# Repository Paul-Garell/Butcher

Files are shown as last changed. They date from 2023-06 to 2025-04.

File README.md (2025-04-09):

# Butcher Lab Cervicheck project

Questions, reach out to George Zeng (gz266@cornell.edu). 

This contains the code to run on Arduino Uno/Due to calculate frequency sweeps using the AD5933 chip.

This repo also will contain the code for communication between the Rasberry pi and Arduino. 

PCB board designs can be found under hardware. 

Uno code (working) can be found under Arduino

Raspberry Pi information can be found under RasPi

Contains code to analyze and present data

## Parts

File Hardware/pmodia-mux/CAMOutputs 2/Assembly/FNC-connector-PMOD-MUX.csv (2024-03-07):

Qty | Value | Device | Package | Parts | Description | AVAILABILITY | CHECK_PRICES | DESCRIPTION | MF | MP | MPN | OC_FARNELL | OC_NEWARK | PACKAGE | POPULARITY | PRICE | PROD_ID | PURCHASE-URL | SNAPEDA_LINK | SPICEPREFIX | VALUE
1 |  | PINHD-1X7/90 | 1X07/90 | JP1 | PIN HEADER |  |  |  |  |  |  |  |  |  | 1
1 | 0.1uF | 0.1UF-0603-25V-(+80/-20%) | 0603 | C1 | 0.1µF ceramic capacitors |  |  |  |  |  |  |  |  |  |  |  | CAP-00810 |  |  |  | 0.1uF
6 | 0.1uF | C-USC0805K | C0805K | C2, C4, C17, C18, C23, C24 | CAPACITOR, American symbol |  |  |  |  |  |  |  |  |  | 19 |  |  |  |  | C
1 | 100K | R-US_R0603 | R0603 | R17 | RESISTOR, American symbol |  |  |  |  |  |  |  |  |  | 77 |  |  |  |  | R
1 | 10k | 10KOHM-0603-1/10W-1% | 0603 | R1 | 10kΩ resistor |  |  |  |  |  |  |  |  |  |  |  | RES-00824 |  |  |  | 10k
5 | 10uF | C-USC0805K | C0805K | C3, C15, C16, C20, C25 | CAPACITOR, American symbol |  |  |  |  |  |  |  |  |  | 19 |  |  |  |  | C
1 | 20 | R-US_R0603 | R0603 | R15 | RESISTOR, American symbol |  |  |  |  |  |  |  |  |  | 77 |  |  |  |  | R
2 | 20K | R-US_R0603 | R0603 | R16, R18 | RESISTOR, American symbol |  |  |  |  |  |  |  |  |  | 77 |  |  |  |  | R
1 | 300 | 0.3OHM-0805-1/8W-1% | 0805 | R10 | 0.3Ω resistor |  |  |  |  |  |  |  |  |  |  |  | RES-11622 |  |  |  | 0.3
1 | 47nF | C-USC0805K | C0805K | C19 | CAPACITOR, American symbol |  |  |  |  |  |  |  |  |  | 19 |  |  |  |  | C
4 | 49.9K | R-US_R0603 | R0603 | R11, R12, R13, R14 | RESISTOR, American symbol |  |  |  |  |  |  |  |  |  | 77 |  |  |  |  | R
2 | 74HC4051BQ | 74HC4051BQ | DHVQFN-16-2.5X3.5MM | U1, U2 | NXP 74HC4051 8-Channel Analog Multiplexer/Demultiplexer |  |  |  |  |  |  |  |  |  |  |  | IC-13334
1 | AD5933 | AD5933 | SSOP16 | U3 | 1 MSPS, 12-Bit Impedance Converter, Network Analyzer
1 | AD8606 | AD8606 | SOIC-8 | U4 | Operational amplifier; 10MHz; 2.7÷5VDC; Channels: 2; SO8 Check availability | In Stock | https://www.snapeda.com/parts/AD8606ARZ/Analog+Devices/view-part/?ref=eda | Precision, Low Noise, RRIO, CMOS Op Amp (Dual) | Analog Devices | AD8606ARZ |  |  |  | SOIC-8 Analog Devices |  | None |  | https://www.snapeda.com/api/url_track_click_mouser/?unipart_id=43414&manufacturer=Analog Devices&part_name=AD8606ARZ&search_term=ad8606 | https://www.snapeda.com/parts/AD8606ARZ/Analog+Devices/view-part/?ref=snap
1 | ADG849THROUHG_HOLE | ADG849THROUHG_HOLE | SOT65P210X110-6N | U$1
1 | ADP150 | ADP150 | SOT95P280X100-5N | U5 | IC REG LINEAR 2V 150MA 5TSOT Check availability | In Stock | https://www.snapeda.com/parts/ADP150AUJZ-2.0-R7/Analog+Devices/view-part/?ref=eda | Ultralow Noise, 150 mA CMOS Linear Regulator | Analog Devices | ADP150AUJZ-2.0-R7 |  |  |  | TSOT-5 Analog Devices |  | None |  | https://www.snapeda.com/api/url_track_click_mouser/?unipart_id=1225884&manufacturer=Analog Devices&part_name=ADP150AUJZ-2.0-R7&search_term=adp150 | https://www.snapeda.com/parts/ADP150AUJZ-2.0-R7/Analog+Devices/view-part/?ref=snap
1 | FH12-16S-0.5SH | FH12-16S-0.5SH | FH12-16S-0.5SH | X1 | 0.5mm Pitch Connectors For FPC/FFC |  |  |  |  |  | FH12-16S-0.5SH(55) | 1324546 | 34M6162 |  | 0

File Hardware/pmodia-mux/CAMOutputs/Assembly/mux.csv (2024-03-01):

Qty | Value | Device | Package | Parts | Description | MF | MPN | OC_FARNELL | OC_NEWARK | POPULARITY
1 | FH12-16S-0.5SH | FH12-16S-0.5SH | FH12-16S-0.5SH | X2 | 0.5mm Pitch Connectors For FPC/FFC |  | FH12-16S-0.5SH(55) | 1324546 | 34M6162 | 0
16 | PADPAD | PADPAD | PAD | U$1, U$2, U$3, U$4, U$5, U$6, U$7, U$8, U$9, U$10, U$11, U$12, U$13, U$14, U$15, U$16

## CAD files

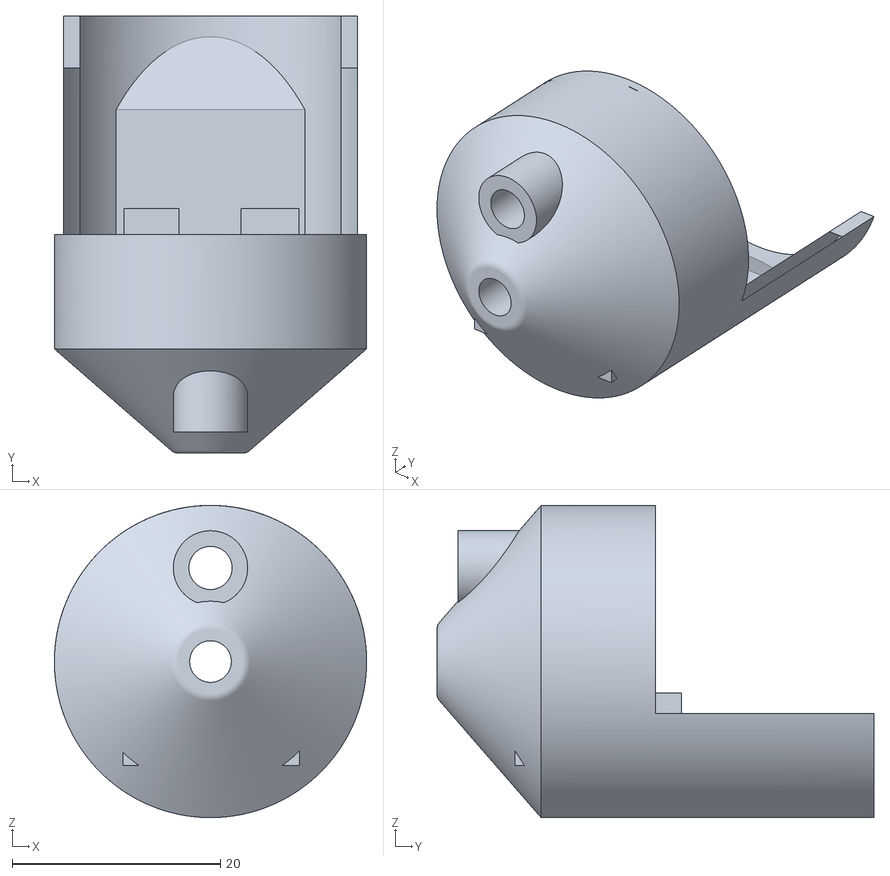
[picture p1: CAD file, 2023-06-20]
Hardware/Cervicheck Probe Tip V1 v20.1.stl
30.0 x 42.0 x 30.0

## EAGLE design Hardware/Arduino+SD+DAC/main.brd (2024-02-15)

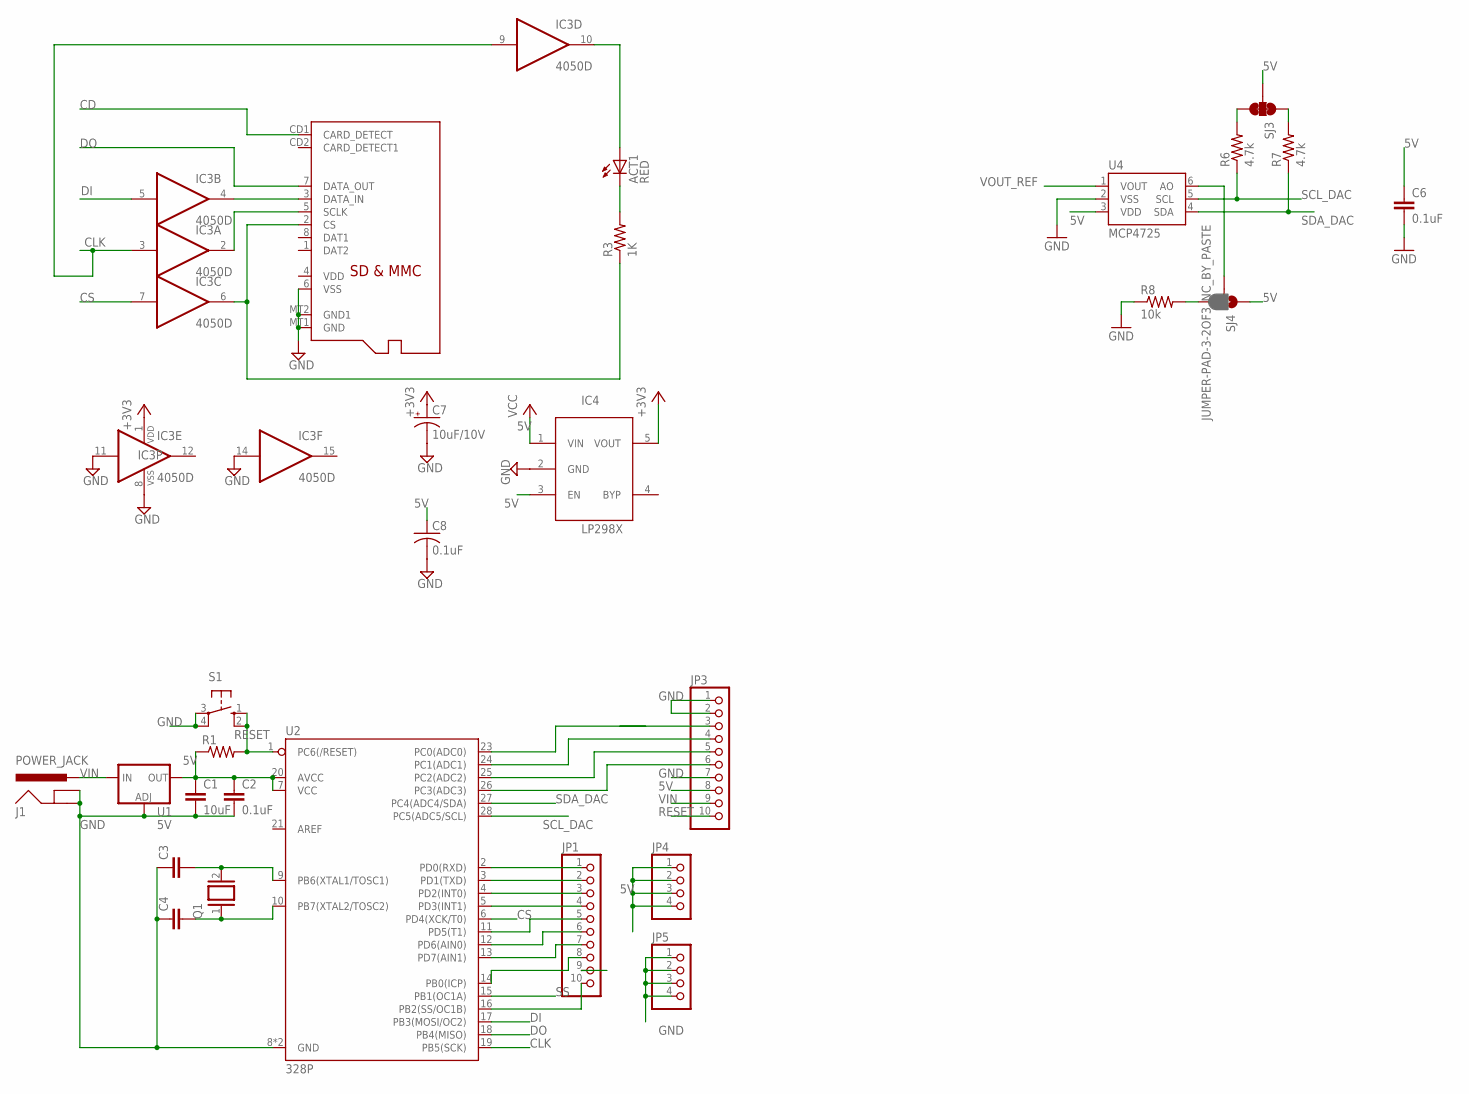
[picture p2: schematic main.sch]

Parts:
ACT1: RED; CHIP-LED0805
C1: 10uF; C025-024X044
C2: 0.1uF; C025-024X044
C3, C4: C-EU025-024X044; C025-024X044
C6: 0.1uF; 0603-CAP
C7: 10uF/10V; A/3216-18R
C8: 0.1uF; C0805K
IC3: 4050D; SO16
IC4: LP298XS; SOT23-5L
J1: POWER_JACK; POWER_JACK_PTH
JP1, JP3: PINHD-1X10; 1X10
JP4, JP5: PINHD-1X4; 1X04
Q1: XTAL/S; QS
R1: R-US_0204/7; 0204/7
R3: 1K; R0805
R6, R7: 4.7k; 0603-RES
R8: 10k; 0603-RES
S1: 10-XX; B3F-10XX
SJ3: JUMPER-PAD-3-NC_BY_TRACE; PAD-JUMPER-3-3OF3_NC_BY_TRACE_YES_SILK_FULL_BOX
SJ4: JUMPER-PAD-3-2OF3_NC_BY_PASTE; PAD-JUMPER-3-2OF3_NC_BY_PASTE_YES_SILK_FULL_BOX
U1: 5V; SOT223
U2: 328P; DIP28
U4: MCP4725; SOT23-6
X2: MICROSD

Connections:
5V: C1.1, C2.1, C6.1, C8.1, IC4.1 (VIN), IC4.3 (EN), JP3.8, JP4.1, JP4.2, JP4.3, JP4.4, R1.1, SJ3.2, SJ4.1, U1.2 (OUT), U1.4 (OUT), U2.7 (VCC), U2.20 (AVCC), U4.3 (VDD)
+3V3: C7.+, IC3.1 (VDD), IC4.5 (VOUT)
CD: X2.CD1 (CARD_DETECT)
CLK: IC3.3 (I), IC3.9 (I), U2.19 (PB5(SCK))
CS: IC3.7 (I), U2.6 (PD4(XCK/T0))
DI: IC3.5 (I), U2.17 (PB3(MOSI/OC2))
DO: U2.18 (PB4(MISO)), X2.7 (DATA_OUT)
GND: C1.2, C2.2, C3.1, C4.1, C6.2, C7.-, C8.2, IC3.8 (VSS), IC3.11 (I), IC3.14 (I), IC4.2 (GND), J1.GND, J1.GNDBREAK, JP3.1, JP3.2, JP3.7, JP5.1, JP5.2, JP5.3, JP5.4, R8.1, S1.3, S1.4 (P1), U1.1 (ADJ), U2.8 (GND), U2.22 (GND), U4.2 (VSS), X2.6 (VSS), X2.MT1 (GND), X2.MT2 (GND1)
unnamed: JP1.1, U2.2 (PD0(RXD))
unnamed: JP3.5, U2.25 (PC2(ADC2))
unnamed: C3.2, Q1.2, U2.9 (PB6(XTAL1/TOSC1))
unnamed: C4.2, Q1.1, U2.10 (PB7(XTAL2/TOSC2))
unnamed: JP1.2, U2.3 (PD1(TXD))
unnamed: JP1.3, U2.4 (PD2(INT0))
unnamed: JP3.6, U2.26 (PC3(ADC3))
unnamed: JP1.4, U2.5 (PD3(INT1))
unnamed: JP1.5, U2.11 (PD5(T1))
unnamed: R7.2, SJ3.1
unnamed: R6.2, SJ3.3
unnamed: SJ4.2, U4.6 (AO)
unnamed: R8.2, SJ4.3
unnamed: JP1.6, U2.12 (PD6(AIN0))
unnamed: JP1.7, U2.13 (PD7(AIN1))
unnamed: JP1.8, U2.14 (PB0(ICP))
unnamed: JP1.10, U2.16 (PB2(SS/OC1B))
unnamed: JP3.4, U2.24 (PC1(ADC1))
unnamed: ACT1.A, IC3.10 (O)
unnamed: IC3.2 (O), X2.5 (SCLK)
unnamed: IC3.6 (O), R3.1, X2.2 (CS)
unnamed: ACT1.C, R3.2
unnamed: IC3.4 (O), X2.3 (DATA_IN)
RESET: JP3.10, R1.2, S1.1 (S), S1.2 (S1), U2.1 (PC6(/RESET))
SCL_DAC: R6.1, U2.28 (PC5(ADC5/SCL)), U4.5 (SCL)
SDA_DAC: R7.1, U2.27 (PC4(ADC4/SDA)), U4.4 (SDA)
SS: JP1.9, U2.15 (PB1(OC1A))
VIN: J1.PWR, JP3.9, U1.3 (IN)
VOUT_REF: U4.1 (VOUT)

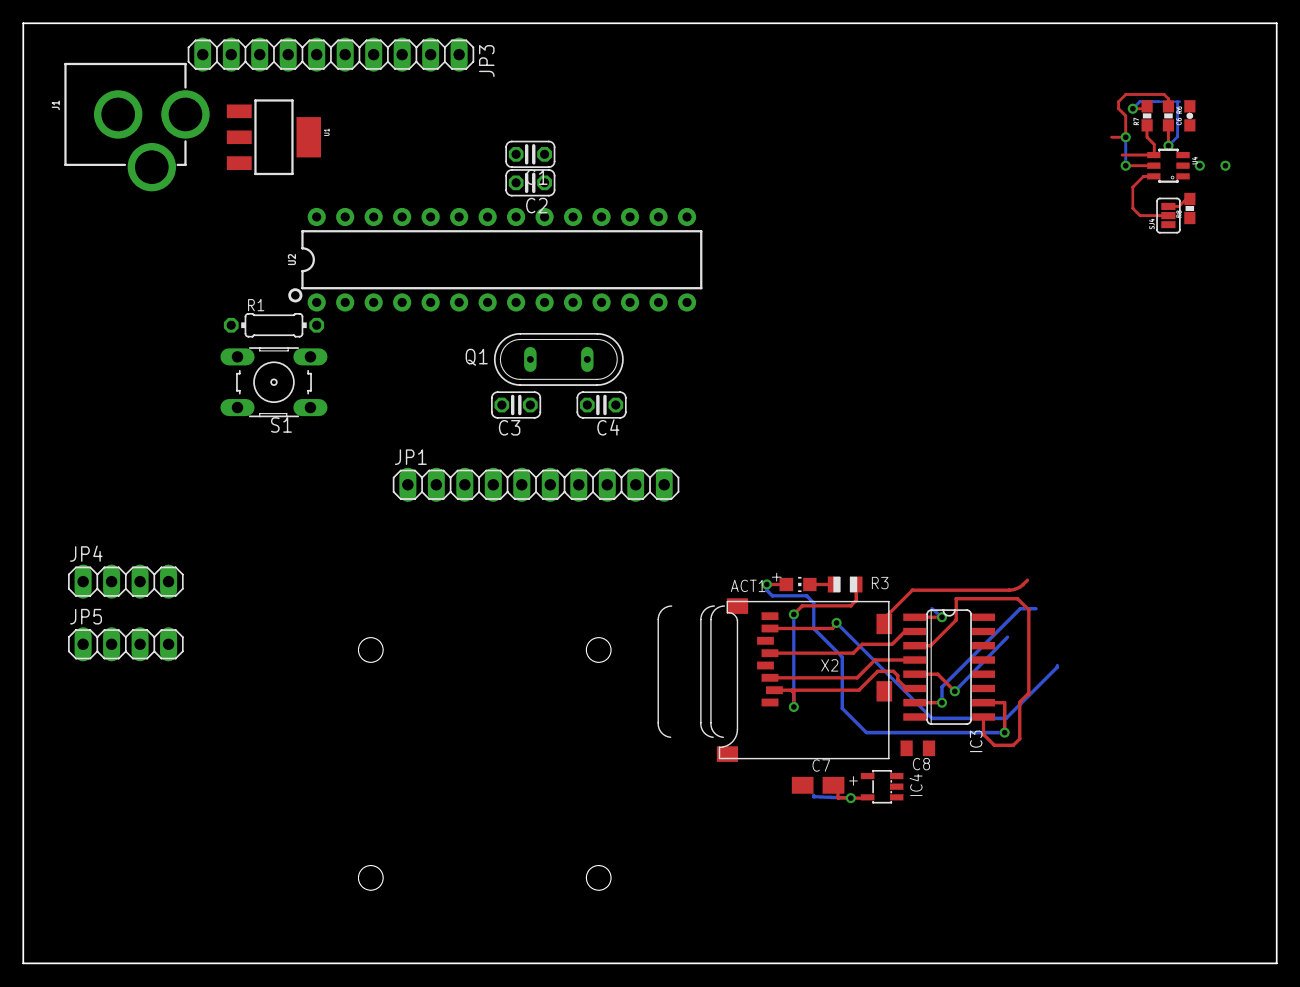
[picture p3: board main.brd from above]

Board: 2 copper layers, 111.8 x 83.8 mm, 28 parts (1 on the bottom side), 35 nets.

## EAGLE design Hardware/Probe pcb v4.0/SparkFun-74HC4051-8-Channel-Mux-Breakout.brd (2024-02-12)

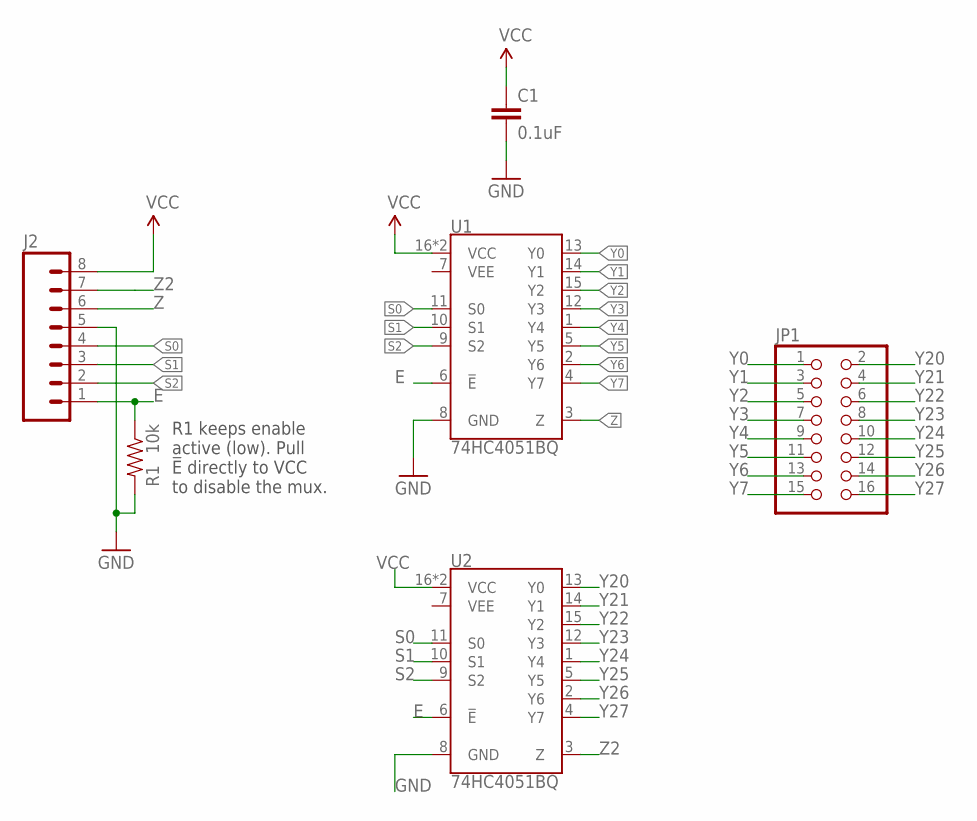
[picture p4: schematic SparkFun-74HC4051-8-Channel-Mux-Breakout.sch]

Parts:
C1: 0.1uF; 0603
J2: M08; 1X08_ROUND
JP1: PINHD-2X8; 2X08
R1: 10k; 0603
U1, U2: 74HC4051BQ; DHVQFN-16-2.5X3.5MM

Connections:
E: J2.1, R1.1, U1.6 (!E!), U2.6 (!E!)
GND: C1.2, J2.5, R1.2, U1.8 (GND), U2.8 (GND)
S0: J2.4, U1.11 (S0), U2.11 (S0)
S1: J2.3, U1.10 (S1), U2.10 (S1)
S2: J2.2, U1.9 (S2), U2.9 (S2)
VCC: C1.1, J2.8, U1.16 (VCC), U1.EP (VCC), U2.16 (VCC), U2.EP (VCC)
Y0: JP1.1, U1.13 (Y0)
Y1: JP1.3, U1.14 (Y1)
Y2: JP1.5, U1.15 (Y2)
Y3: JP1.7, U1.12 (Y3)
Y4: JP1.9, U1.1 (Y4)
Y5: JP1.11, U1.5 (Y5)
Y6: JP1.13, U1.2 (Y6)
Y7: JP1.15, U1.4 (Y7)
Y20: JP1.2, U2.13 (Y0)
Y21: JP1.4, U2.14 (Y1)
Y22: JP1.6, U2.15 (Y2)
Y23: JP1.8, U2.12 (Y3)
Y24: JP1.10, U2.1 (Y4)
Y25: JP1.12, U2.5 (Y5)
Y26: JP1.14, U2.2 (Y6)
Y27: JP1.16, U2.4 (Y7)
Z: J2.6, U1.3 (Z)
Z2: J2.7, U2.3 (Z)

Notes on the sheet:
R1 keeps enable active (low). Pull !E! directly to VCC to disable the mux.

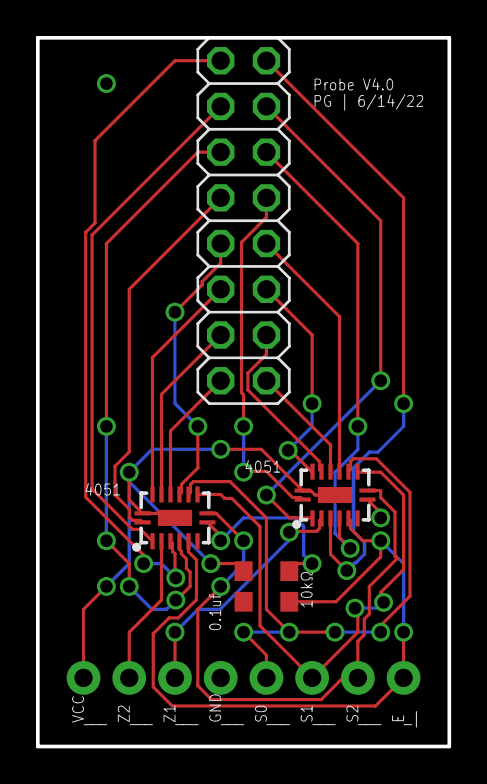
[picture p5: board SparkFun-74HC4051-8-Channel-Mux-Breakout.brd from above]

Board: 2 copper layers, 22.9 x 39.4 mm, 6 parts (1 on the bottom side), 24 nets.

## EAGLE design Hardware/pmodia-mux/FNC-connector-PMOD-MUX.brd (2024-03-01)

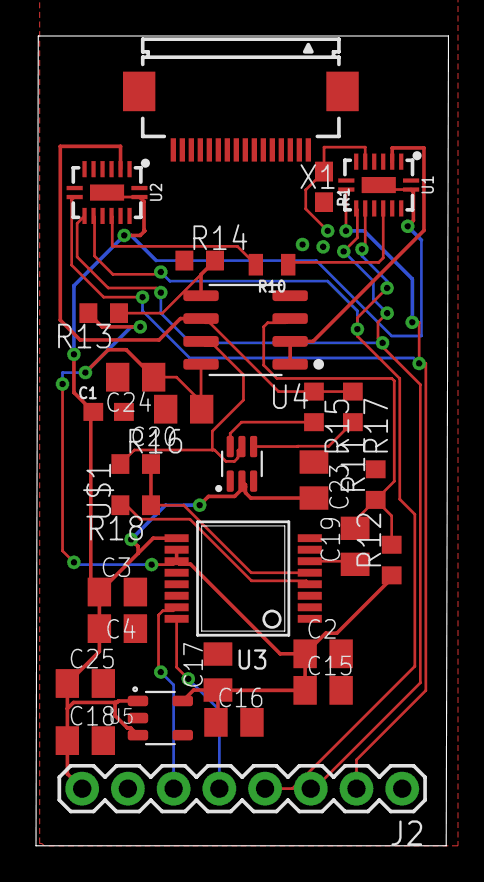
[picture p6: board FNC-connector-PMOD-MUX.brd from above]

Board: 2 copper layers, 22.9 x 45.0 mm, 31 parts (0 on the bottom side), 35 nets.

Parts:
C1: 0.1uF; 0603
C2, C4, C17, C18, C23, C24: 0.1uF; C0805K
C3, C15, C16, C20, C25: 10uF; C0805K
C19: 47nF; C0805K
J2: 1X08_ROUND
R1: 10k; 0603
R10: 300; 0805
R11, R12, R13, R14: 49.9K; R0603
R15: 20; R0603
R16, R18: 20K; R0603
R17: 100K; R0603
U1, U2: 74HC4051BQ; DHVQFN-16-2.5X3.5MM
U3: AD5933; SSOP16
U4: AD8606; SOIC-8
U5: ADP150; SOT95P280X100-5N
U$1: ADG849THROUHG_HOLE; SOT65P210X110-6N
X1: FH12-16S-0.5SH

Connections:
E: R1.1, U1.6, U2.6
GND: C1.2, C2.2, C3.2, C4.2, C15.2, C16.2, C17.2, C18.2, C20.2, C23.1, C24.2, C25.2, J2.1, R1.2, R11.2, R14.1, U1.8, U2.8, U3.12, U3.14, U4.4, U5.2, U$1.3
INBP: R13.1, R14.2, U4.5
unnamed: C19.1, U3.6
unnamed: C19.2, R11.1, R12.2, U4.3
unnamed: R18.2, U3.4
unnamed: R15.2, U$1.6
unnamed: R17.2, U$1.4
unnamed: R16.1, U4.7, U$1.5
S0: J2.4, U1.11, U2.11
S1: J2.3, U1.10, U2.10
S2: J2.2, U1.9, U2.9
SCL: J2.5, U3.16
SDA: J2.6, U3.15
VCC: C1.1, C3.1, C4.1, C18.1, C23.2, C25.1, J2.8, U1.16, U1.EP, U2.16, U2.EP, U3.9, U5.1, U5.3, U$1.2
VCC3V0: C2.1, C15.1, C16.1, C17.1, C20.1, C24.1, R12.1, R13.2, U3.10, U3.11, U4.8, U5.5
VIN: R16.2, R18.1, U3.5
Y0: R10.1, U1.13, X1.8
Y1: U1.14, X1.7
Y2: U1.15, X1.6
Y3: U1.12, X1.5
Y4: U1.1, X1.4
Y5: U1.5, X1.3
Y6: U1.2, X1.2
Y7: U1.4, X1.1
Y20: R10.2, U2.13, X1.9
Y21: U2.14, X1.10
Y22: U2.15, X1.11
Y23: U2.12, X1.12
Y24: U2.1, X1.13
Y25: U2.5, X1.14
Y26: U2.2, X1.15
Y27: U2.4, X1.16
Z: U1.3, U4.1, U4.2
Z2: R15.1, R17.1, U2.3, U4.6

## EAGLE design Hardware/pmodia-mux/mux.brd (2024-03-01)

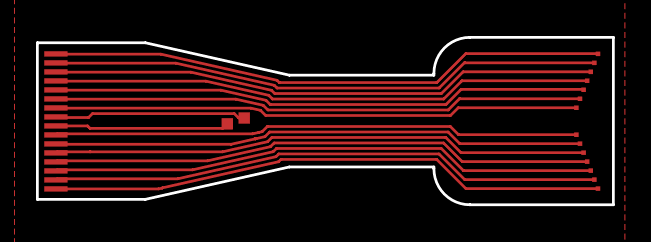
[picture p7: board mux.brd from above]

Board: 2 copper layers, 32.0 x 9.3 mm, 17 parts (0 on the bottom side), 16 nets.

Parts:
U$1, U$2, U$3, U$4, U$5, U$6, U$7, U$8, U$9, U$10, U$11, U$12, U$13, U$14, U$15, U$16: PADPAD; PAD
X2: FH12-16S-0.5SH

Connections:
unnamed: U$1.P$1, X2.1
unnamed: U$2.P$1, X2.2
unnamed: U$3.P$1, X2.3
unnamed: U$4.P$1, X2.4
unnamed: U$5.P$1, X2.5
unnamed: U$6.P$1, X2.6
unnamed: U$7.P$1, X2.7
unnamed: U$8.P$1, X2.8
unnamed: U$9.P$1, X2.9
unnamed: U$10.P$1, X2.10
unnamed: U$11.P$1, X2.11
unnamed: U$12.P$1, X2.12
unnamed: U$13.P$1, X2.13
unnamed: U$14.P$1, X2.14
unnamed: U$15.P$1, X2.15
unnamed: U$16.P$1, X2.16

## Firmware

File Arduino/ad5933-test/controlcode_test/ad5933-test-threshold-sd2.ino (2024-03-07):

#include <Wire.h>
#include "AD5933.h"
#include <Adafruit_MCP4725.h>
#include <SD.h>
#include <SPI.h>

#define START_FREQ  (10000)
#define FREQ_INCR   (5000)
#define NUM_INCR    (18)
#define REF_RESIST  (300)
#define DAC_RESOLUTION (9)

bool setter = true;
int follow = 0;

// Mux setup
int Signal = 5;
int i;
int sL[3] = {8, 9, 10};
int MUXtable[8][3] = {
  {0, 0, 0}, {1, 0, 0}, {0, 1, 0}, {1, 1, 0},
  {0, 0, 1}, {1, 0, 1}, {0, 1, 1}, {1, 1, 1}
};

// DAC setup for Pressure regulator
int DACp = 0;
double Curvoltage = .5;

Adafruit_MCP4725 dac;

double gain[NUM_INCR + 1];
int phase[NUM_INCR + 1];

// Pressure variable for barometric sensor
const int pressureInput = A1;  // where the pressure will be sensed
const int pressureZ = 102;    // the minimum voltage for 0 pressure
const int pressureM = 921;    // the maxium voltage for 15psi
const int pressurePSI = 15;  
float pressure;  // where we want to store the value from the incoming pressure transducer
int normalP = 0; // placeholder

File dataFile;
const double impedanceMax = 500.0; //CHANGED: threshold to detect air
bool impedanceCheck = false; 

String filename = "data.csv";
void setup(void)
{
  pinMode(Signal, OUTPUT);
  for (i = 0; i < 3; i++) pinMode(sL[i], OUTPUT);
  pinMode(A2, OUTPUT);
  digitalWrite(A2, LOW);
  dac.begin(0x60);
  
  // Begin serial at 9600 baud for output
  Serial.begin(9600);
  // Begin I2C
  Wire.begin();
  // Select SD card pin
  const int chipSelectPin = 4;
  // Perform initial configuration. Fail if any one of these fail.
  Serial.println("AD5933 Test Started!");

  if (!(AD5933::reset() &&
        AD5933::setInternalClock(true) &&
        AD5933::setStartFrequency(START_FREQ) &&
        AD5933::setIncrementFrequency(FREQ_INCR) &&
        AD5933::setNumberIncrements(NUM_INCR) &&
        AD5933::setPGAGain(PGA_GAIN_X1)))
  {
    Serial.println("FAILED in initialization!");
    while (true);
  }
  // Set mux to the calibration output (select Y0) (300 ohm resistor installed on board)
  digitalWrite(sL[0], MUXtable[0][0]);
  digitalWrite(sL[1], MUXtable[0][1]);
  digitalWrite(sL[2], MUXtable[0][2]);
  
  // Perform calibration sweep
  if (AD5933::calibrate(gain, phase, REF_RESIST, NUM_INCR + 1))
    Serial.println("Calibrated!");
  else
    Serial.println("Calibration failed...");

  // Initialize the SD card
  if (SD.begin(chipSelectPin)) {
    Serial.println("SD card module is connected.");
  } else {
    Serial.println("SD card module is not detected. Check connections.");
  }

  // Open a new file for writing
  dataFile = SD.open(filename, FILE_WRITE);
  if (dataFile) {
    Serial.println("Created data.csv file.");
  } else {
    Serial.println("Failed to create data.csv file!");
  }
  
  // Write the column headers to the file
  dataFile.println("Pin, Time, Pressure, Impedance");
  
  // Close the file
  dataFile.close();
}

int pinNum = 1;

void loop(void) {
  dac.setVoltage((Curvoltage * 4095) / 5, false);
  while (pinNum < 9) {
    selection(pinNum);
    if (frequencySweepEasy(pinNum)) break;
    pinNum++;
  }
  pinNum = 1;
  Curvoltage += .5;
  if (Curvoltage > 2.9) {
    Curvoltage = 0.5;
  }
}

bool frequencySweepEasy(int pin) {
  // Create arrays to hold the data
  int real[NUM_INCR + 1], imag[NUM_INCR + 1];

  // Perform the frequency sweep
  if (AD5933::frequencySweep(real, imag, NUM_INCR + 1)) {
    // Open the data file in append mode
    dataFile = SD.open("data.csv", FILE_WRITE);
    if (!dataFile) {
      // Calculating and printing out the pressure information
      int cfreq = START_FREQ / 1000;
      dataFile.print(pin);
      dataFile.print(", ");
      dataFile.print(millis());
      dataFile.print(", ");
      dataFile.print(normalP, 1);
      dataFile.print(", ");

      Serial.print(millis());
      Serial.print(", ");
      Serial.print(pin);
      Serial.print(", ");
      Serial.print(normalP, 1);

      for (int i = 0; i < NUM_INCR + 1; i++, cfreq += FREQ_INCR / 1000) {
        pressure = analogRead(pressureInput);
        pressure = (pressure - pressureZ) * 15 / (pressureM - pressureZ);
        normalP = abs((pressure * 6.89476) - 98);
        dataFile.print(", ");

        // Compute impedance
        double magnitude = sqrt(pow(real[i], 2) + pow(imag[i], 2));
        double impedance = 1 / (magnitude * gain[i]);

        dataFile.print(impedance);
        dataFile.print(", ");

        Serial.print(", ");
        Serial.print(impedance);
        Serial.println(" "); 

        // Determine if impedance is too high
        if (impedance > impedanceMax){ 
          Serial.print(" ");
          return true;
        }
      }
      dataFile.println(" ");
      Serial.println(" "); 
      // Close the file
      Serial.flush();
      dataFile.close();
    }
  }
  return false;
}

void selection(int j) {
  digitalWrite(sL[0], MUXtable[j][0]);
  digitalWrite(sL[1], MUXtable[j][1]);
  digitalWrite(sL[2], MUXtable[j][2]);
}

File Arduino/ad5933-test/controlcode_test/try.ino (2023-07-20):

#include <Wire.h>
#include "AD5933.h"
#include <Adafruit_MCP4725.h>

#define START_FREQ  (10000)
#define FREQ_INCR   (5000)
#define NUM_INCR    (18)
#define REF_RESIST  (300)

// Threshold setup
int impedanceCheck; // Define a high resistance here

// Mux setup
int Signal = 5;
int i;
int sL[3] = {8, 9, 10};
int MUXtable[8][3] = {
  {0, 0, 0}, {1, 0, 0}, {0, 1, 0}, {1, 1, 0},
  {0, 0, 1}, {1, 0, 1}, {0, 1, 1}, {1, 1, 1}
};

// DAC setup for Pressure regulator
int DACp = 0;
double Curvoltage = 0.5;

Adafruit_MCP4725 dac;
#define DAC_RESOLUTION (9)

double gain[NUM_INCR + 1];
int phase[NUM_INCR + 1];

// Pressure variable for barometric sensor
const int pressureInput = A1;
const int pressureZ = 102;
const int pressureM = 921;
const int pressurePSI = 15;
float pressure;
int normalP = 0;

void calibrateAD5933() {
  if (!(AD5933::reset() &&
        AD5933::setInternalClock(true) &&
        AD5933::setStartFrequency(START_FREQ) &&
        AD5933::setIncrementFrequency(FREQ_INCR) &&
        AD5933::setNumberIncrements(NUM_INCR) &&
        AD5933::setPGAGain(PGA_GAIN_X1)))
  {
    Serial.println("FAILED in initialization!");
    while (true) ;
  }

  if (AD5933::calibrate(gain, phase, REF_RESIST, NUM_INCR + 1)) {
    Serial.println("Calibrated!");
  } else {
    Serial.println("Calibration failed...");
  }

  // Store calibrated values in global variables
  int cfreq = START_FREQ / 1000; // Starting frequency
  for (int i = 0; i < NUM_INCR + 1; i++, cfreq += FREQ_INCR / 1000) {
    // Compute impedance
    double magnitude = sqrt(pow(gain[i], 2) + pow(phase[i], 2));
    gain[i] = 1 / (magnitude * gain[i]);
  }

  // Calculate and store the high impedance check value
  double magnitude = sqrt(pow(gain[0], 2) + pow(phase[0], 2));
  double impedance = 1 / (magnitude * gain[0]);
  impedanceCheck = (int)impedance;
}

void setup(void) {
  Serial.begin(9600);
  pinMode(Signal, OUTPUT);
  for (i = 0; i < 4; i++) pinMode(sL[i], OUTPUT);

  pinMode(A2, OUTPUT);
  digitalWrite(A2, LOW);
  dac.begin(0x60);
  Wire.begin();
  Serial.println("AD5933 Test Started!");

  // Call the calibration function once during setup
  calibrateAD5933();
}

int curChannel = 1;
void loop(void) {
  dac.setVoltage((Curvoltage * 4095) / 5, false);
  for (curChannel = 1; curChannel <= 8; curChannel++) {
    Serial.print(curChannel);
    selection(curChannel);
    if (frequencySweepEasy(curChannel)) break;
  }

  Curvoltage += 0.5; // Increment voltage counter
  if (Curvoltage > 2.9) {
    Curvoltage = 0.5;
  }
}

bool frequencySweepEasy(int pin) {
  // Create arrays to hold the data
  int real[NUM_INCR + 1], imag[NUM_INCR + 1];

  // Perform the frequency sweep
  if (AD5933::frequencySweep(real, imag, NUM_INCR + 1)) {
    // Print the frequency data
    int cfreq = START_FREQ / 1000;
    // Calculating and printing out the pressure information
    pressure = analogRead(pressureInput); // will read the value from the input pin
    pressure = (pressure - pressureZ) * 15 / (pressureM - pressureZ); // convert analog reading to psi
    normalP = abs((pressure * 6.89476) - 98); // normalize?

    Serial.print(millis());
    Serial.print(", ");
    Serial.print(pin);
    Serial.print(", ");
    Serial.print(normalP, 1); // converting to kPa while also printing (units kPa)

    for (int i = 0; i < NUM_INCR + 1; i++, cfreq += FREQ_INCR / 1000) {

      // Use the stored calibrated values to compute impedance
      double magnitude = sqrt(pow(real[i], 2) + pow(imag[i], 2));
      double impedance = 1 / (magnitude * gain[i]);
      Serial.print(", ");
      Serial.print(impedance);

      // Checker
      if (impedance > impedanceCheck) {
        Serial.println(" ");
        return true;
      }
    }
    Serial.println(" ");
  }
  return false;
}

void selection(int j) {
  digitalWrite(sL[0], MUXtable[j][0]);
  digitalWrite(sL[1], MUXtable[j][1]);
  digitalWrite(sL[2], MUXtable[j][2]);
}

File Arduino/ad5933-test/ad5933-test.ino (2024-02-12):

/*
  ad5933-test
    Reads impedance values from the AD5933 over I2C and prints them serially.
*/
// 200, 1.1, 5.1 20000
#include <Wire.h>
#include "AD5933.h"
#define START_FREQ  (10000)
#define FREQ_INCR   (5000)
#define NUM_INCR    (10) //was 18, changing to 10 for demo
#define REF_RESIST  (300)
bool setter = true;
int follow = 0;

//Mux setup
int Signal = 5; int i; //int n;
int sL[3] = {8, 9, 10}; //int sU[4] = {13,10,11,12};
int MUXtable[8][3] = {{0, 0, 0}, {1, 0, 0}, {0, 1, 0}, {1, 1, 0},
  {0, 0, 1}, {1, 0, 1}, {0, 1, 1}, {1, 1, 1}
};


//DAC setup for Pressure regulator
int DACp = 0;
double Curvoltage = .5;
#include <Adafruit_MCP4725.h>
Adafruit_MCP4725 dac;
#define DAC_RESOLUTION (9)



double gain[NUM_INCR + 1];
int phase[NUM_INCR + 1];

//Pressure variable for barometric sensor
const int pressureInput = A1;  // where the pressure will be sensed
const int pressureZ = 102;    // the minimum voltage for 0 pressure
const int pressureM = 921;    // the maxium voltage for 15psi
const int pressurePSI = 15;  
float pressure;  // where we want to store the value from the incoming pressure transducer
int normalP = 0; //placeholder


void setup(void)
{

  //Mux setup
  pinMode(Signal, OUTPUT);
  for (i = 0; i < 4; i++) pinMode(sL[i], OUTPUT);
  //for(n=0; n<4; n++) pinMode(sU[n], OUTPUT);


  //DAC setup (pressure regulator)
  //pinMode(DAC1, OUTPUT); /*this is for the arduino DUE
  //analogWriteResolution(12);   //** I think this is messing with the setup
  pinMode(A2, OUTPUT);
  digitalWrite(A2, LOW);
  dac.begin(0x60);


// Begin serial at 9600 baud for output
  Serial.begin(9600);

  // Begin I2C
  Wire.begin();

  
  Serial.println("AD5933 Test Started!");


  // Perform initial configuration. Fail if any one of these fail.
  if (!(AD5933::reset() &&
        AD5933::setInternalClock(true) &&
        AD5933::setStartFrequency(START_FREQ) &&
        AD5933::setIncrementFrequency(FREQ_INCR) &&
        AD5933::setNumberIncrements(NUM_INCR) &&
        AD5933::setPGAGain(PGA_GAIN_X1)))
  {
    Serial.println("FAILED in initialization!");
    while (true) ;
  }

  /** //Debugging tool
    if (!AD5933::reset()) follow = 1; setter = false;
    if (setter && !AD5933::setInternalClock(true))  follow = 2; setter = false;
    if (setter && !AD5933::setStartFrequency(START_FREQ)) follow = 3; setter = false;
    if (setter && !AD5933::setIncrementFrequency(FREQ_INCR)) follow = 4; setter = false;
    if (setter && !AD5933::setNumberIncrements(NUM_INCR)) follow = 5; setter = false;
    if (setter && !AD5933::setPGAGain(PGA_GAIN_X1)) follow = 6; setter = false;
    while(!setter) {
    Serial.println(follow);
    }
  */



  //Set mux to the calibration output (select Y0) (300 ohm resistor installed on baord)
  digitalWrite(sL[0], MUXtable[0][0]);
  digitalWrite(sL[1], MUXtable[0][1]);
  digitalWrite(sL[2], MUXtable[0][2]);


  // Perform calibration sweep
  if (AD5933::calibrate(gain, phase, REF_RESIST, NUM_INCR + 1))
    Serial.println("Calibrated!");
  else
    Serial.println("Calibration failed...");
}

void loop(void) {
  
  
  //Setup delay in between cycles NOT IN USE
  for (i = 0; i < 0; i++) {
    Serial.println("Delay");
    delay(1000);
  }


  //Set select for Mux
  //int i = 4; selection(i);
  //for (DACp = .3; DACp < 3; DACp = DACp + .2) {
    
    //analogWrite(DAC1, DACp);
    //delay(1000);

    
    dac.setVoltage((Curvoltage*4095)/5, false);
    Serial.println((Curvoltage*4095)/5);
    for (i = 0; i < 3; i++) {
      selection(i);
    }

    
    Curvoltage = Curvoltage + .5; // voltage counter
    if (Curvoltage > 2.9) {
      Curvoltage = 0.5;
    }
  //}


  // Easy to use method for frequency sweep
  //frequencySweepEasy();

  // Delay
  //delay(10000);

  // Complex but more robust method for frequency sweep
  //frequencySweepRaw();

  // Delay
  //delay(5000);
}

// Easy way to do a frequency sweep. Does an entire frequency sweep at once and
// stores the data into arrays for processing afterwards. This is easy-to-use,
// but doesn't allow you to process data in real time.
void frequencySweepEasy(int pin) {





  // Create arrays to hold the data
  int real[NUM_INCR + 1], imag[NUM_INCR + 1];

  // Perform the frequency sweep
  if (AD5933::frequencySweep(real, imag, NUM_INCR + 1)) {
    // Print the frequency data
    int cfreq = START_FREQ / 1000;

    Serial.print(pin);
    Serial.print(", ");
    Serial.print(normalP, 1); // converting to kPa while also printing (units kPa)

    for (int i = 0; i < NUM_INCR + 1; i++, cfreq += FREQ_INCR / 1000) {

      //claculating and printing out the pressure information
      pressure = analogRead(pressureInput); // will read the value from the input pin
      pressure = (pressure - pressureZ) * 15 / (pressureM - pressureZ); // convert analog reading to psi
      normalP = abs((pressure * 6.89476) - 98); // normalize?
      //Serial.print("pin: ");


      //Serial.print("  "); // label to the number
      //Serial.print(cfreq);
      //Serial.print(": R=");
      //Serial.print(",");
      //Serial.print(real[i]);
      //Serial.print("/I=");
      Serial.print(", ");
      //Serial.print(imag[i]);

      // Compute impedance
      double magnitude = sqrt(pow(real[i], 2) + pow(imag[i], 2));
      double impedance = 1 / (magnitude * gain[i]);
      //Serial.print("  |Z|=");
      //Serial.print(",");
      Serial.print(impedance);
    }
    Serial.println(" ");
  } else {
    //Serial.println("Frequency sweep failed...");
  }
}
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

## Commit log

2023-06-20 Add Probe
    [SparkFun-74HC4051-8-Channel-Mux-Breakout.sch]
2023-06-20 Add probe stl
    [Cervicheck Probe Tip V1 v20.1.stl]
2023-06-22 Update ad5933-test-new.ino
    change pin
2023-06-28 Update ad5933-test-sd.ino
    -added a time elapsed column, before impedance and after pressure columns
2023-07-11 Update sd5933-test-threshold-sd.ino
    serial print statements for testing
2023-07-11 Update sd5933-test-threshold-sd.ino
    Commented out serial prints
2023-07-16 Update ad5933-test-threshold.ino
    add calibration
2023-09-21 update layout
    [Redesign-8Ch-Mux-Breakout-PMODIA.sch]
2023-10-19 [Update] start routing board
    [SparkFun-74HC4051-8-Channel-Mux-Breakout.brd]
2023-11-02 Add files via upload
    pad library and mux schematic
    [mux.sch]
2024-02-12 new Schematic
    [Redesign-8Ch-Mux-Breakout-PMODIA.brd, SparkFun-74HC4051-8-Channel-Mux-Breakout.brd, main.brd, main.sch]
2024-02-20 Finished Flex PCB
    [mux.brd]
2024-03-01 Updated names
    [FNC-connector-PMOD-MUX.brd, FNC-connector-PMOD-MUX.sch]
2024-03-07 Start main
    [FNC-connector-PMOD-MUX.csv, PnP_FNC-connector-PMOD-MUX_front.csv, copper_bottom.gbr, copper_top.gbr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]
2024-10-18 Create PressureSweepV1
2025-01-23 Create PressureSweep_V2

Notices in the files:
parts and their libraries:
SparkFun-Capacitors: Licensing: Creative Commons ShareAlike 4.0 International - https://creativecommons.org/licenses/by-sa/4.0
